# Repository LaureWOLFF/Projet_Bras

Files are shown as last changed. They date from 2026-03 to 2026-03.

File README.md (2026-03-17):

# 🦾 Robot Control via Electromyographic (EMG) Signals

Ce projet, réalisé dans le cadre de la deuxième année d'ingénieur à l'**ENSEA (Cergy)**, porte sur la conception et la réalisation d'un capteur électromyographique (EMG) complet et l'activation d'un robot par ces signaux. L'objectif est de capturer l'activité électrique des muscles du bras pour permettre, à terme, le contrôle du robot.

## 📌 Présentation du Projet
Le système permet de détecter les signaux bioélectriques de très faible amplitudes émis lors d'une contraction musculaire, de les traiter analogiquement pour les rendre exploitables, puis de les numériser via un microcontrôleur **ESP32**.

### 🛠 Caractéristiques
* **Cible :** Muscles du bras (biceps et ceux de l'avant-bras).
* **Signal d'entrée :** Amplitude de $10\mu\text{V}$ à $5\text{mV}$, fréquence de 10 Hz à 500 Hz.
* **Traitement Analogique :** * Amplification d'instrumentation (Gain élevé).
    * Filtrage passe-bande (élimination du bruit 50 Hz et des hautes fréquences).
    * Redressement et lissage du signal (enveloppe du signal).
* **Numérisation :** ADC de l'ESP32 (échantillonnage et traitement logiciel).

---

## 🏗 Architecture du capteur EMG

Le projet est actuellement divisé en plusieurs blocs:

1.  **Étage de Pré-amplification :** Utilisation d'un amplificateur d'instrumentation pour extraire le signal différentiel des électrodes.
2.  **Filtrage Actif :** Nettoyage du signal pour ne garder que la bande utile de l'EMG.
3.  **Redresseur de précision :** Conversion du signal alternatif en signal continu (enveloppe de contraction).
4.  **Adaptation de tension :** Ajustement du signal vers une plage 0-3.3V compatible avec l'ESP32.

---
## 🤖 Cahine d'information Capteur --> Robot

Pour piloter le robot, l'information circule à travers les étapes suivantes :

1. **Acquisition :** Captation des micro-tensions sur la peau via les électrodes.
2. **Traitement Analogique :** Traitement via le capteur EMG.
3. **Numérisation :** L'ESP32 convertit le signal analogique en données numériques via son ADC.
4. **Interprétation :** Analyse du seuil de tension pour détecter une contraction ou un relâchement.
5. **Communication :** Envoi des commandes via Bluetooth/Wi-Fi vers le système de contrôle du robot.
6. **Actionnement  :** Le robot exécute le mouvement correspondant (ex: fermeture de la pince).

---
## 🚀 État d'avancement à la mi-parcours (S7)

* ✅ **Étude théorique :** Analyse des signaux EMG et définition des besoins d'amplification.
* ✅ **Choix des composants :** Passage sur des AOP type TL08x pour la réalisation physique.
* ✅ **Conception d'un prototype:** Saisie de schéma et assignation des empreintes (SOIC-8 / 0805) sur KiCad pour soudure au four.
* 🔲 **Poursuite du projet :** Finition du prototype, réalisation du PCB, tests réels avec électrodes et développement du code de traitement sur l'ESP32 (filtres numériques, Bluetooth/Wi-Fi).

---

## 📋 Travail effectué lors du S8
* **Simulation complète du captuer EMG**: Pour palier aux dysfonctionnement du prototype, on a simuler entierment le composant jusqu'à avoir le comportment voulu.
* **Réalisation du PCB**: le capteur et une carte de commande pour assebler tous les éléments
* **Travail informatique**: écriture de code afin de faire bouger le robot en fonction des mouvement (ouverture de la main, contration du muscle).
  
---

## 🔝Evolution de ce projet et axes de développement

---

## 📦 Technologies utilisées
* **CAO Électronique :** LTspice, Niryo, KiCad 9.0.
* **Matériel :** ESP32, MyoWear, composants actifs (AOP TL081) et passifs.
* **Langages :** C (Arduino IDE / PlatformIO), ROS\ROS2, Python.

---

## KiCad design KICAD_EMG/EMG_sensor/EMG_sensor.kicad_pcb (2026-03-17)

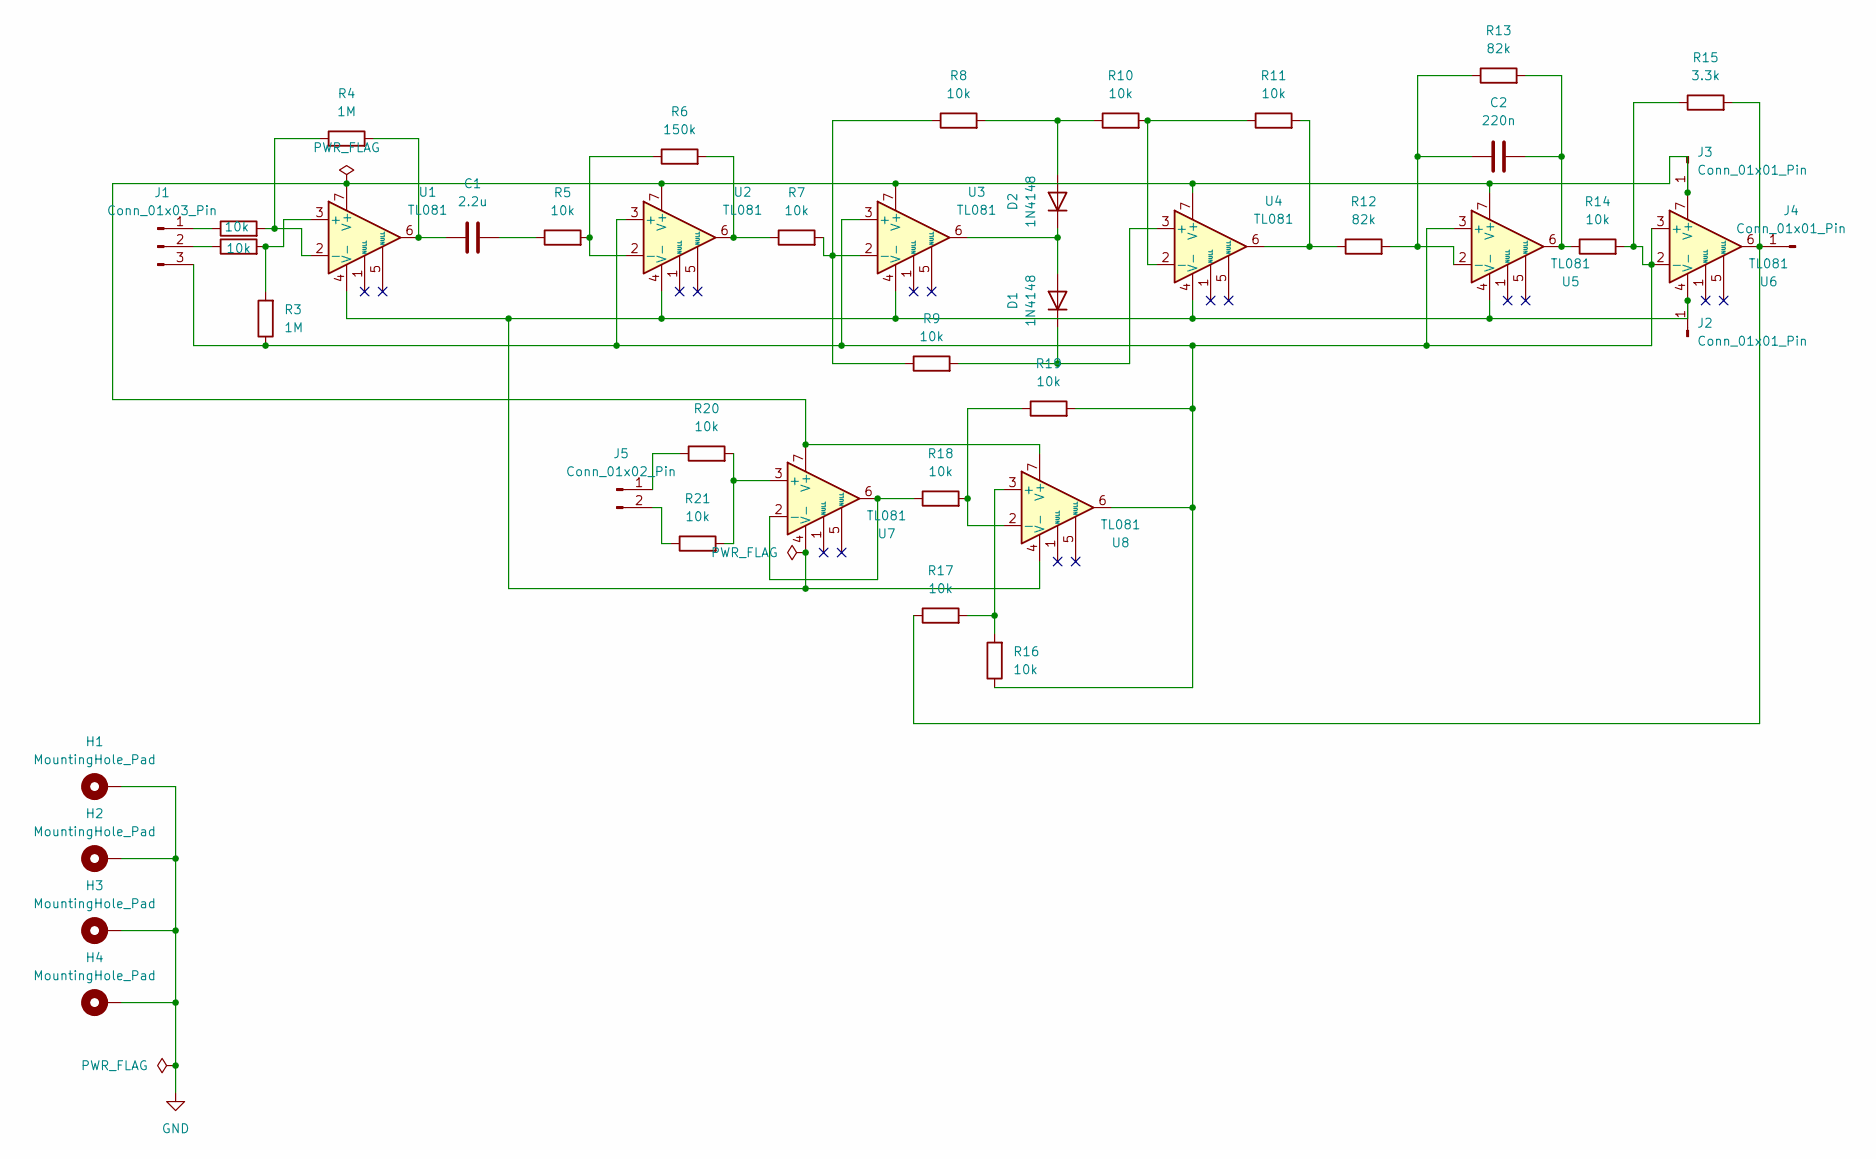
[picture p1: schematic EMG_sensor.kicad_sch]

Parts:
C1: 2.2u; C_0402_1005Metric_Pad0.74x0.62mm_HandSolder
C2: 220n; C_0402_1005Metric_Pad0.74x0.62mm_HandSolder
D1, D2: 1N4148; D_SOD-123
H1, H2, H3, H4: MountingHole_Pad; MountingHole_2.2mm_M2_Pad
J1: Conn_01x03_Pin; FanPinHeader_1x03_P2.54mm_Vertical
J2, J3, J4: Conn_01x01_Pin; PinHeader_1x01_P2.54mm_Vertical
J5: Conn_01x02_Pin; JST_EH_B2B-EH-A_1x02_P2.50mm_Vertical
R1, R2, R5, R7, R8, R9, R10, R11, R14, R16, R17, R18, R19, R20, R21: 10k; R_0402_1005Metric_Pad0.72x0.64mm_HandSolder
R3, R4: 1M; R_0402_1005Metric_Pad0.72x0.64mm_HandSolder
R6: 150k; R_0402_1005Metric_Pad0.72x0.64mm_HandSolder
R12, R13: 82k; R_0402_1005Metric_Pad0.72x0.64mm_HandSolder
R15: 3.3k; R_0402_1005Metric_Pad0.72x0.64mm_HandSolder
U1, U2, U3, U4, U5, U6, U7, U8: TL081; SO-8_3.9x4.9mm_P1.27mm

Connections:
GND: H1.1, H2.1, H3.1, H4.1
unnamed: C1.1, R4.2, U1.6
unnamed: C1.2, R5.1
unnamed: C2.1, R13.2, R14.1, U5.6
unnamed: D1.2 (A), D2.1 (K), U3.6
unnamed: D1.1 (K), R9.2, U4.3 (+)
unnamed: D2.2 (A), R8.2, R10.1
unnamed: J1.1, R1.1
unnamed: J1.2, R2.1
unnamed: J1.3, R3.1, R14.2, R15.1, R16.1, R19.2, U2.3 (+), U3.3 (+), U5.3 (+), U6.2 (-), U6.3 (+), U8.6
unnamed: J2.1, U1.4 (V-), U2.4 (V-), U3.4 (V-), U4.4 (V-), U5.4 (V-), U6.4 (V-), U7.4 (V-), U8.4 (V-)
unnamed: J3.1, U1.7 (V+), U2.7 (V+), U3.7 (V+), U4.7 (V+), U5.7 (V+), U6.7 (V+), U7.7 (V+), U8.7 (V+)
unnamed: J4.1, R15.2, R17.1, U6.6
unnamed: J5.1, R20.1
unnamed: J5.2, R21.1
unnamed: R6.2, R7.1, U2.6
unnamed: R11.2, R12.1, U4.6
unnamed: R2.2, R3.2, U1.3 (+)
unnamed: R1.2, R4.1, U1.2 (-)
unnamed: R5.2, R6.1, U2.2 (-)
unnamed: R7.2, R8.1, R9.1, U3.2 (-)
unnamed: R10.2, R11.1, U4.2 (-)
unnamed: C2.2, R12.2, R13.1, U5.2 (-)
unnamed: R20.2, R21.2, U7.3 (+)
unnamed: R18.1, U7.2 (-), U7.6
unnamed: R16.2, R17.2, U8.3 (+)
unnamed: R18.2, R19.1, U8.2 (-)

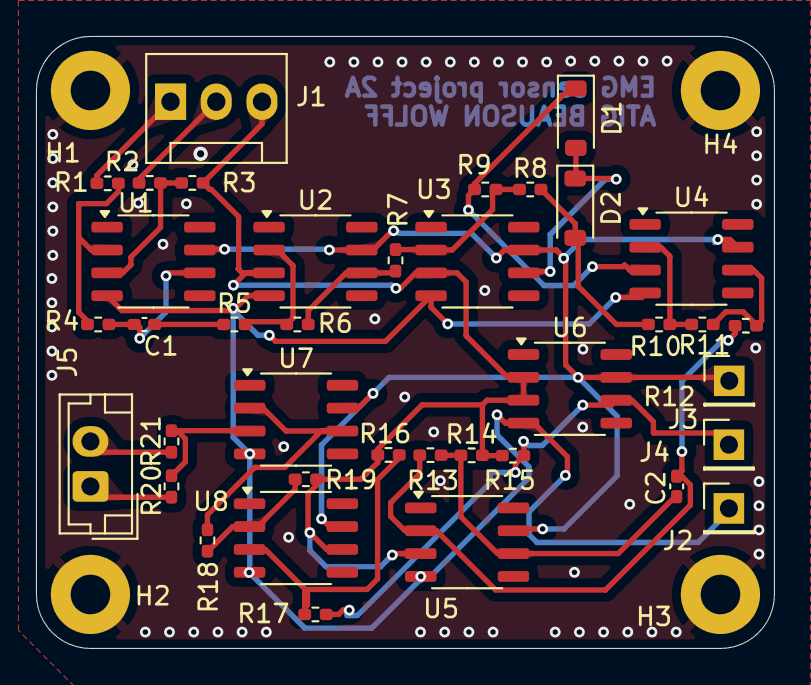
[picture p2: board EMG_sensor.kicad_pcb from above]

Board: 2 copper layers, 41.0 x 34.0 mm, 42 parts (0 on the bottom side), 27 nets.

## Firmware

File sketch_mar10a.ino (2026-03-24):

#include <WiFi.h>

// --- CONFIGURATION RÉSEAU ---
const char* ssid = "NIRYONED1";
const char* password = "niryorobot";
const char* host = "10.10.10.10";
const int port = 5005;

IPAddress local_IP(10, 10, 10, 60);
IPAddress gateway(10, 10, 10, 10);
IPAddress subnet(255, 255, 255, 0);

const int EMG_PIN = 34;

// --- PARAMÈTRES (À ajuster en regardant le graphique) ---
int SEUIL_ACTION = 2500; // Le pic pour déclencher l'action
int SEUIL_REPOS = 1500;  // Le niveau où on considère le muscle détendu

// --- VARIABLES D'ÉTAT ---
bool pinceFermee = false;        // L'état actuel de la pince
bool contractionEnCours = false; // Le "verrou" anti-répétition

void setup() {
    Serial.begin(115200);
    analogReadResolution(12);

    // Connexion WiFi
    WiFi.config(local_IP, gateway, subnet);
    WiFi.mode(WIFI_STA);
    WiFi.setMinSecurity(WIFI_AUTH_WPA_PSK);
    WiFi.begin(ssid, password);

    // Attente de la connexion (Le traceur série ignorera ces points)
    while (WiFi.status() != WL_CONNECTED) {
        delay(500);
        Serial.print(".");
    }
    Serial.println("\n✅ Connecté ! Robot + Graphique activés.");
}

void loop() {
    WiFiClient client;
    int emgValue = analogRead(EMG_PIN);

    // ==========================================
    // 1. LOGIQUE DE DÉCISION & ENVOI AU ROBOT
    // ==========================================
    
    // Détection d'un nouveau pic d'effort
    if (emgValue > SEUIL_ACTION && !contractionEnCours) {
        contractionEnCours = true; // On verrouille
        
        pinceFermee = !pinceFermee; // On inverse l'état de la pince

        // Envoi de l'ordre au robot
        if (client.connect(host, port)) {
            if (pinceFermee) {
                client.print("CLOSE");
            } else {
                client.print("OPEN");
            }
            client.stop();
        }
        // Grosse pause pour le robot. 
        // Note: Le graphique va "figer" pendant une demi-seconde ici, c'est normal !
        delay(500); 
    }
    
    // Détection du relâchement total du muscle
    else if (emgValue < SEUIL_REPOS && contractionEnCours) {
        contractionEnCours = false; // On déverrouille le système
        delay(50);
    }


    // ==========================================
    // 2. AFFICHAGE POUR LE TRACEUR SÉRIE
    // ==========================================
    
    // On crée une valeur (0 ou 4000) pour voir l'état de la pince sur l'écran
    int etatPinceGraphique = pinceFermee ? 4000 : 0;

    // Format strict pour le Traceur Série : "Nom:Valeur, Nom:Valeur"
    Serial.print("Signal_Brut:");
    Serial.print(emgValue);
    Serial.print(",");
    
    Serial.print("Seuil_Action:");
    Serial.print(SEUIL_ACTION);
    Serial.print(",");
    
    Serial.print("Seuil_Repos:");
    Serial.print(SEUIL_REPOS);
    Serial.print(",");
    
    Serial.print("ETAT_PINCE:");
    Serial.println(etatPinceGraphique);

    delay(20); // Lecture à 50Hz pour un graphique fluide
}

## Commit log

2026-02-10 Add TCP server for ESP32 MOVE signal handling
2026-02-10 Add ESP32 code for WiFi connection and voltage monitoring
    This code connects an ESP32 to a WiFi network, reads an analog voltage from a specified pin, and sends a command to a server when the voltage exceeds a threshold.
2026-03-02 Ajout denombreux fichiers dont la première ver. du PCB
    [EMG_sensor.kicad_pcb, EMG_sensor.kicad_sch, PDB_sensor.kicad_pcb, PDB_sensor.kicad_sch]
2026-03-10 le PCB avec les piste à 0.3 et 0 erreur
    [EMG_sensor-B_Cu.gbr, EMG_sensor-B_Mask.gbr, EMG_sensor-B_Paste.gbr, EMG_sensor-B_Silkscreen.gbr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]
2026-03-17 PCB modifié et envoyé en ticket
    [EMG_sensor-B_Cu.gbr, EMG_sensor-B_Mask.gbr, EMG_sensor-B_Paste.gbr, EMG_sensor-B_Silkscreen.gbr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]
2026-03-24 Add files via upload
    code de décision ouverture/fermeture avec seuils de L'ESP 32.
